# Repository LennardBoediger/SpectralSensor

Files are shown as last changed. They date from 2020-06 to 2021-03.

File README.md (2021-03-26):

# Spectral Measurement Platform
## This is my Bachelorthesis: "Entwicklung und Realisierung eines Messsystems mit den Sensoren AS7261 und AS72651 von AMS"

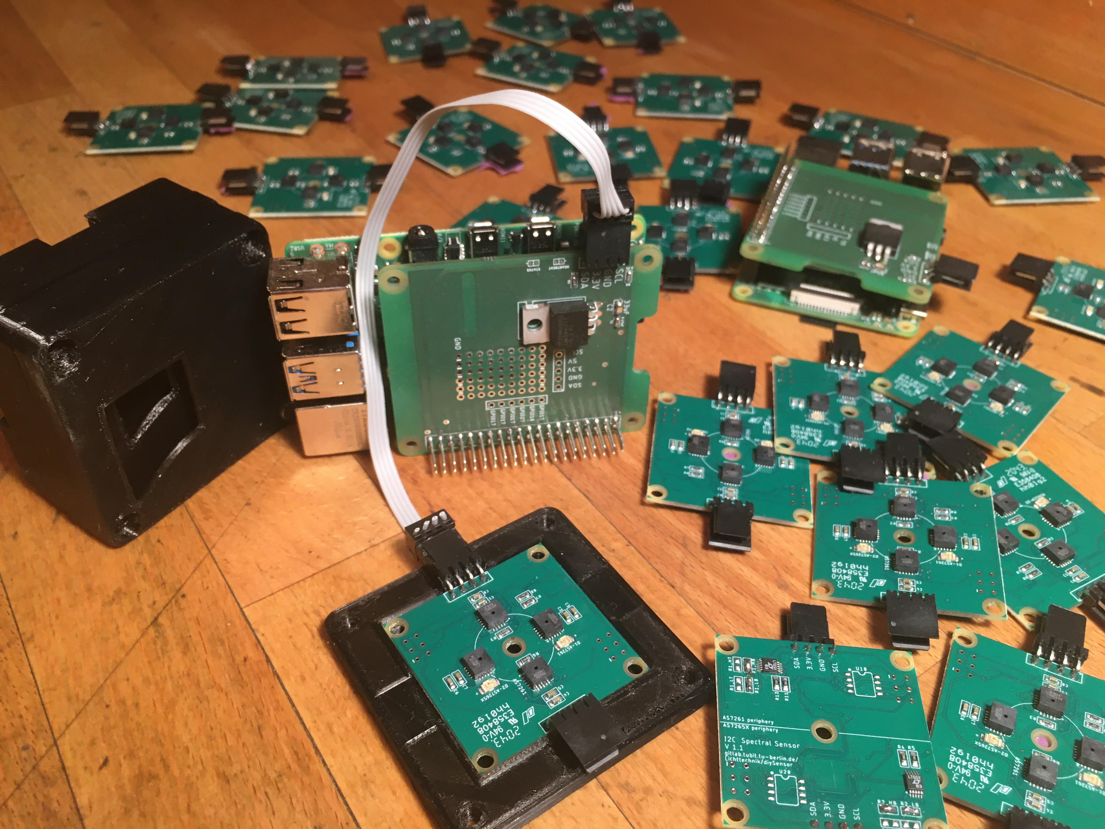
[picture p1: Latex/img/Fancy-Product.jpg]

The goal of this work is to develop a spectral sensor platform using the AS7261 and AS72651, which can be used modularly for different 
research purposes, but especially for sky measurements. Since it is not possible to measure in several directions in the sky at the same 
time with only one of the AS7261 (or AS72651) sensors without mechanical components, it must be ensured that a large number of sensors can be 
combined into a sensor array in order to be able to measure with directional resolution. The resulting sensor platform uses a Raspberry Pi 4 as central 
control unit, which communicates with external sensor boards via I2C.

The final sensor platform will be able to differentiate 21 spectral channels of incident light from up to 20 different directions.

## Grafana WebInterface 

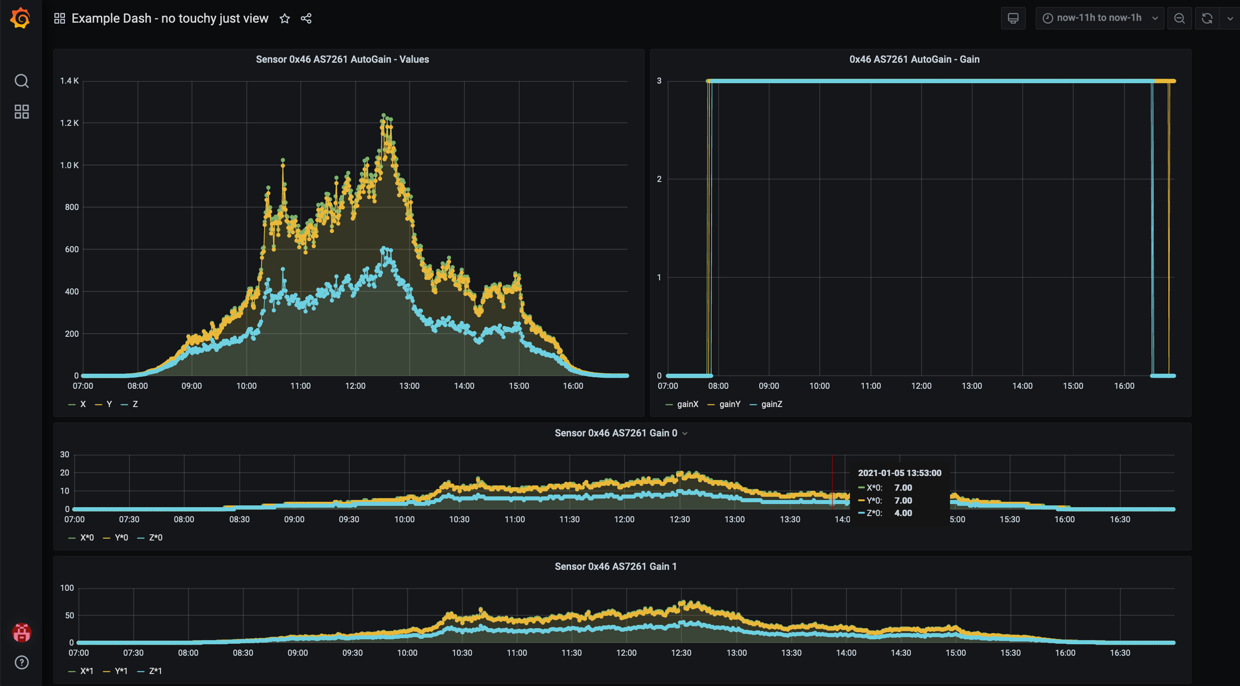
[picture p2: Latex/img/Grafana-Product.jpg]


## Auto Gain
To increase the usable light intensity range, the AutoGain mode can be used.</br>
Measurements are made in all 4 possible gains, the most accurate measured value is selected for each channel. This value is adjusted to the maximum gain with the function matchValueTo-MaxGain to allow a continuous representation of the output.
```c
for (uint8_t gain_i = 0; gain_i < 4; ++gain_i){         // going through every gain
                settings(s[i].address, integrationValue, gain_i); // apply settings integrationValue is fix gain is 0-3
                MeasurementFromAdress(s[i].address);            // initiate measurement from current adress
                AS7261_measurement[gain_i] = getAS7261Measurement(s[i].address, measurement_time, gain_i, 1);    // get data and save to array
            }
            
```

## Usage
Flash the SD image</br>
Attach 1-20 Sensorboards in sereries</br>
Connect to the Pi over SSH</br>
start a detachable screen </br>
make compiles and runs the software</br>
</br>
ssh pi@[IP-ADRESSE]</br>
git clone https://github.com/LennardBoediger/SpectralSensor</br>
cd SpectralSensor </br>
screen</br>
make</br>

Attatch the screen with `screen -r`</br>
Follow the instructions to change the setting and start the measurement</br>
The Webinterface can be found at port 3000 `http://[RASPBERRY_PI-IP]:3000`
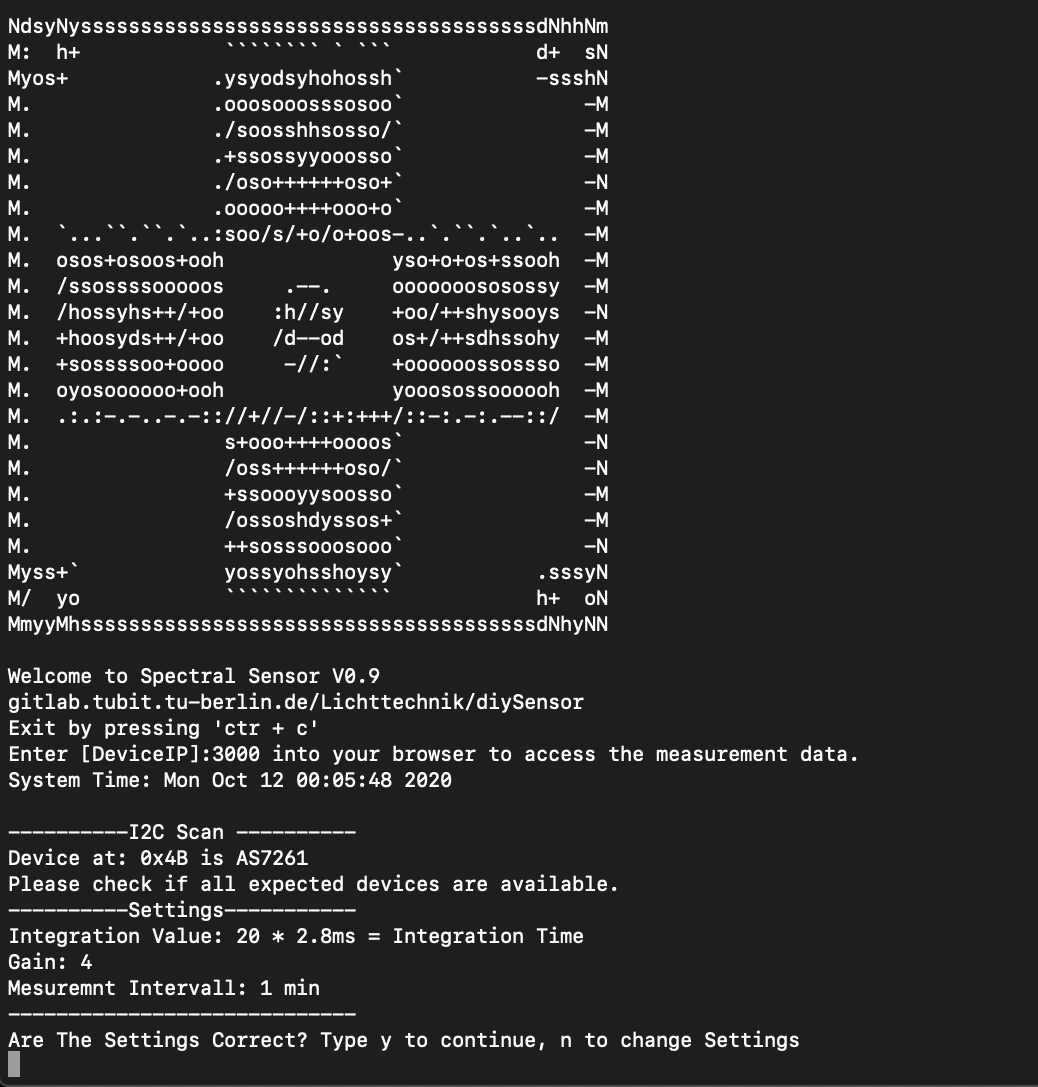
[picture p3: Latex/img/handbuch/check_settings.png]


# Hardware
### Sensorboard
I2C Lanes in Red.</br>
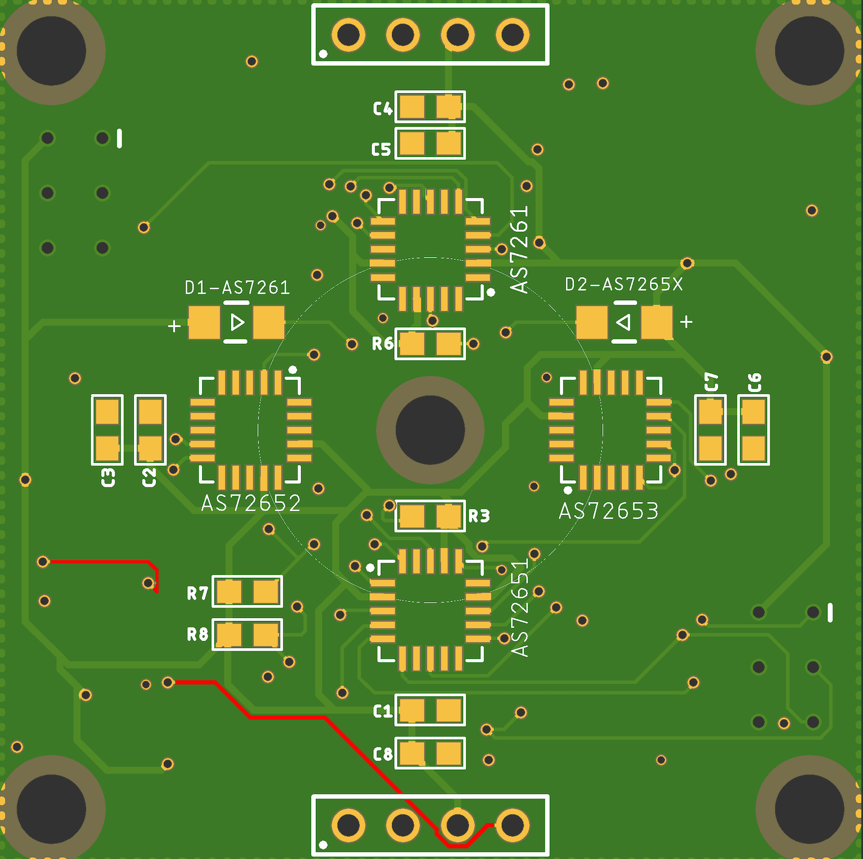
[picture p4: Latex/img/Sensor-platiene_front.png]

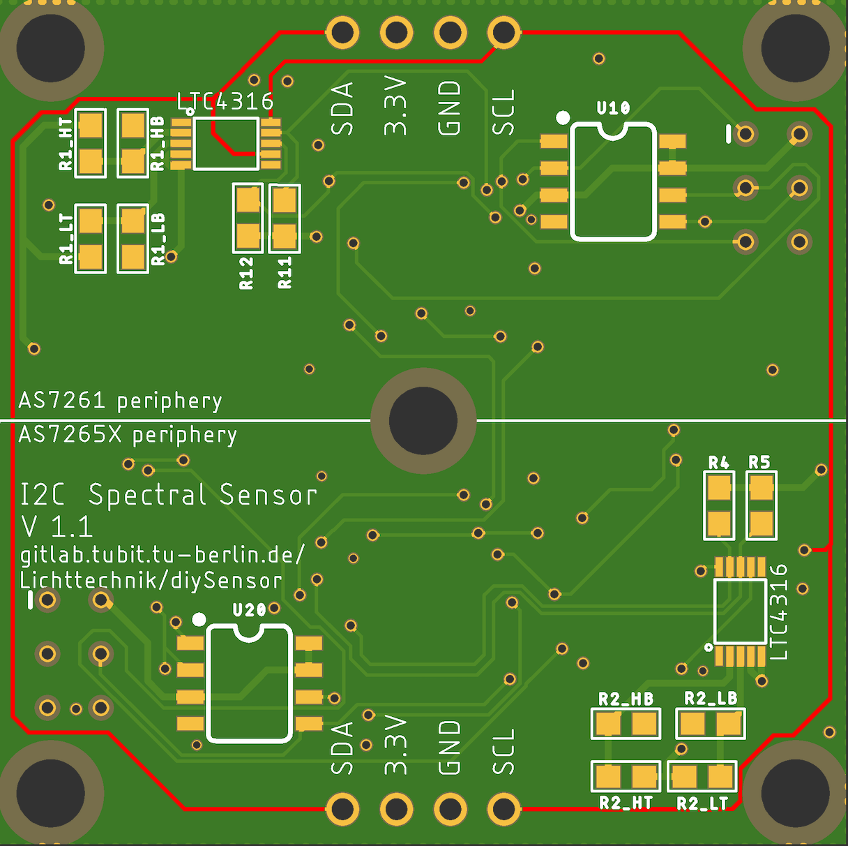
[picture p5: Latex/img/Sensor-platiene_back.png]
right

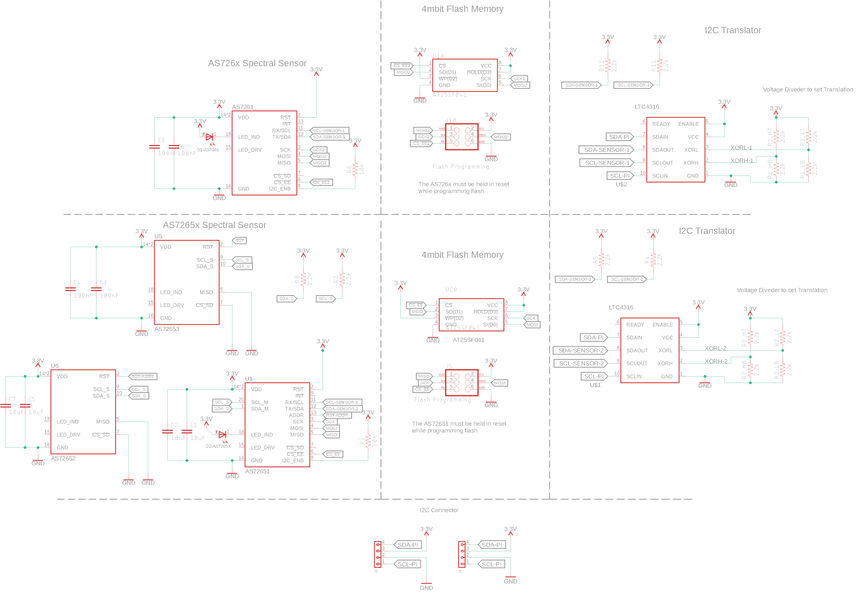
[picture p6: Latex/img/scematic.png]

### Pi-Shield
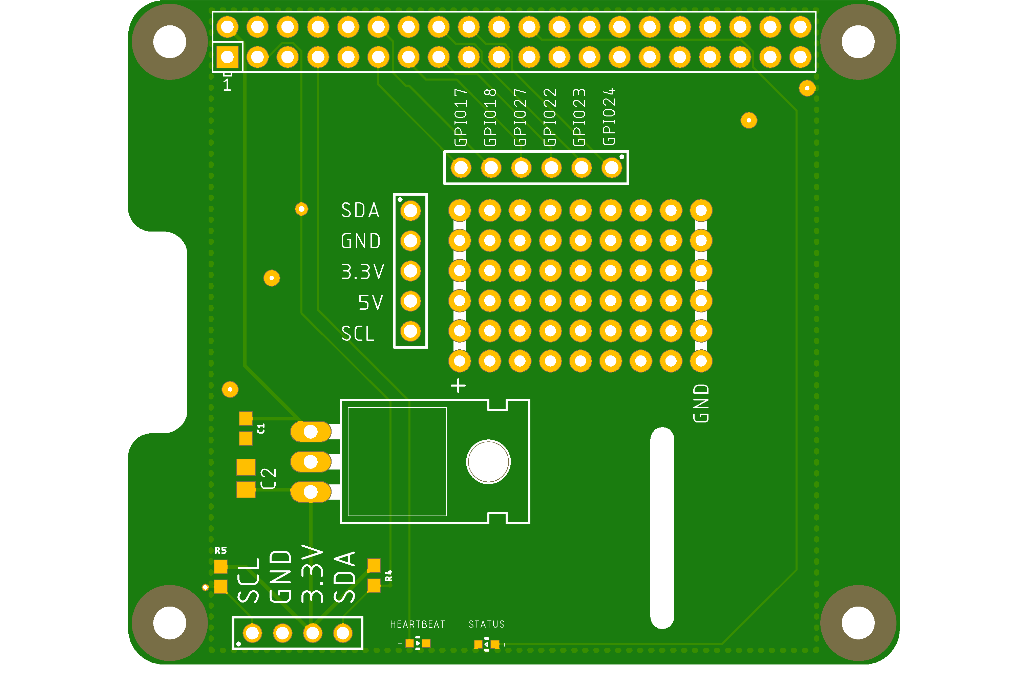
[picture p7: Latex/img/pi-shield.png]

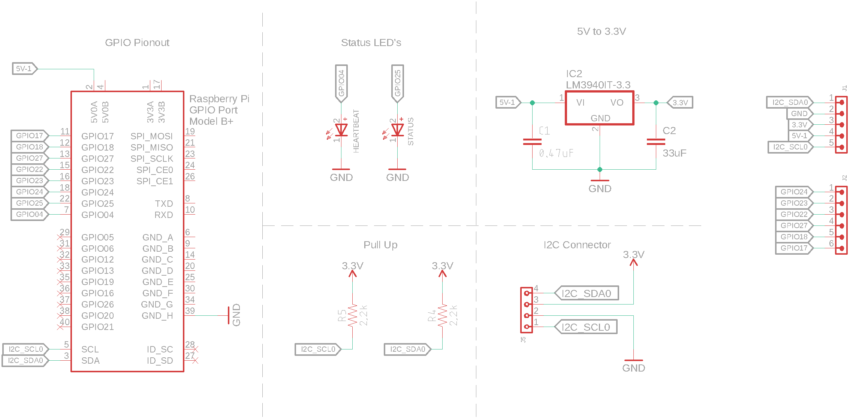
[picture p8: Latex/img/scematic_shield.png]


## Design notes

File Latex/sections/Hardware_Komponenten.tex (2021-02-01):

\subsection{Sensoren}\label{Sensoren}

\begin{wrapfigure}{R}{0.3\textwidth}
\centering
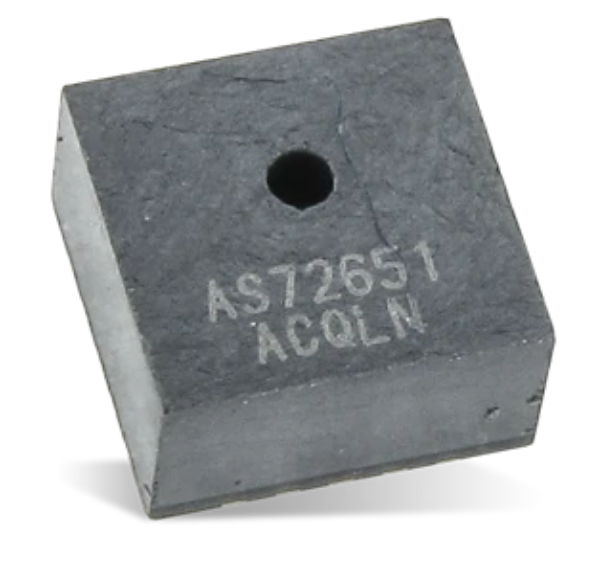
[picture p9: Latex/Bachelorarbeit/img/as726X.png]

 \caption{AS726X \cite{Datenblatt_AS7265X}}
\label{fig:AS726X}
\end{wrapfigure}

Die Sensoren aus der AS726X Reihe sind in der Lage Licht, also elektromagnetische Strahlung, zu messen. 
In jedem Sensor sind 6 Photodioden verbaut. 
Vor jeder Photodiode ist ein Silizium-Interferenzfilter montiert, welcher wie ein Bandpassfilter arbeitet. Er ist nur für einen bestimmten Ausschnitt des Lichtspektrums durchlässig.
Jeder Baustein enthält einen Analog-Digital-Wandler mit 16 Bit Auflösung, der den Photostrom aus den Fotodioden integriert. Nach Abschluss einer Messung wird das integrierte Ergebnis in die entsprechenden RAW Data Register übertragen.\\
So kann über das beschriebene Sensorarray die farbliche Zusammensetzung des eingestrahlten Lichts erfasst werden.

\begin{figure}[H]
\centering
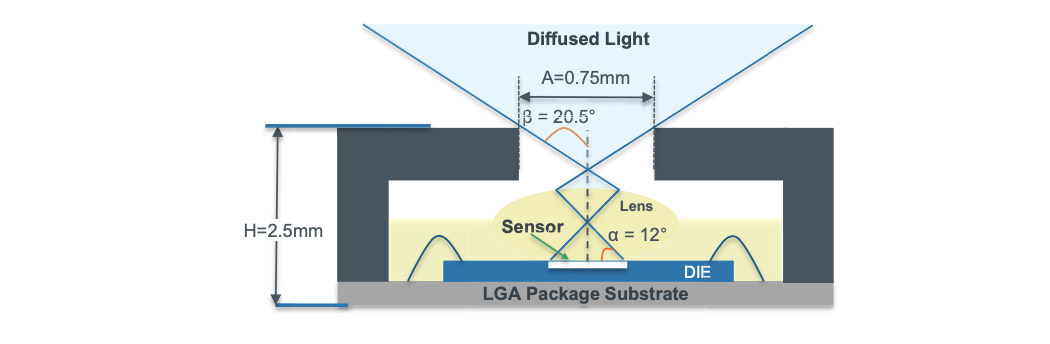
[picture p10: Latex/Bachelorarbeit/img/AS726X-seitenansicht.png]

\caption{Seitenasicht AS726X\cite{Datenblatt_AS7265X}}
\label{fig:Seitenasicht-AS726X}
\end{figure}

\noindent Wie in Abbildung \ref{fig:Seitenasicht-AS726X} dargestellt, fällt das Licht durch die Öffnung in der Mitte des Sensors ein. Eine intern verbaute Linse verteilt das Lich auf die Interferenzfilter. Die Genauigkeit der Filter verändert sich je nach Einstrahlwinkel, daher ist es wichtig vor den Sensor noch eine Streuscheibe zu montieren.\\
Die so gemessenen Daten können über UART oder I2C an einen Mikrocontroller übertragen werden. Da über UART nur ein Gerät verbunden werden kann, eignet sich aber für diesen Anwendungsfall nur die I2C Schnittstelle.\\
\newpage
\noindent Alle Sensoren erhalten vom Hersteller dieselbe, nicht veränderbare I2C Adresse: 0x49. Daher muss ein I2C Translator genutzt werden, welcher es ermöglicht mehrere Sensoren im gleichen Bussystem zu adressieren (siehe Abschnitt \ref{I2C-Translator}).\\

\noindent Die Modelle unterscheiden sich durch die verbauten Silizium-Interferenzfilter, also die unterscheidbaren Wellenlängenbereiche sowie in der benötigten Peripherie.
Die grundsätzliche Messmethode ist aber immer gleich.
Im Folgenden werden die verwendeten Sensoren AS7261 (siehe Abschnitt \ref{AS7261}) sowie der AS7265X (siehe Abschnitt \ref{AS7265X}) beschrieben.\\
Intern im Sensor werden aus den RAW-Werten kalibrierte Werte berechnet, jedoch wird keine ausreichende Dokumentation bereitgestellt.
Daher konnte keine konsistente Korrelation zwischen RAW- und kalibrierten Werten ermittelt werden, weshalb sie im Messaufbau nicht verwendet werden.

%\begin{wrapfigure}{L}{0.3\textwidth}
%\centering
%    \caption{Seitenasicht AS726X}
% \includegraphics[width=0.7\textwidth]{img/AS726X-seitenansicht.png}
% \caption*{Quelle: Datenblatt AS7261}
%  \label{fig:AS726X}
%\end{wrapfigure}
\newpage
\subsubsection{AS7261}\label{AS7261}
Das Sensorarray des AS7261 unterscheidet zwischen X, Y, Z, Clear, Dark und NIR.
Wobei X, Y und Z nach CIE 1931 definiert sind.
Clear ist eine Fotodiode ohne Filter.
Dark ist eine abgedunkelte Fotodiode und wird nur verwendet um störende Einflüsse zu detektieren.
NIR steht für Near-infrared  (Nah-Infrarot).\\

\begin{figure}[H]
  \centering
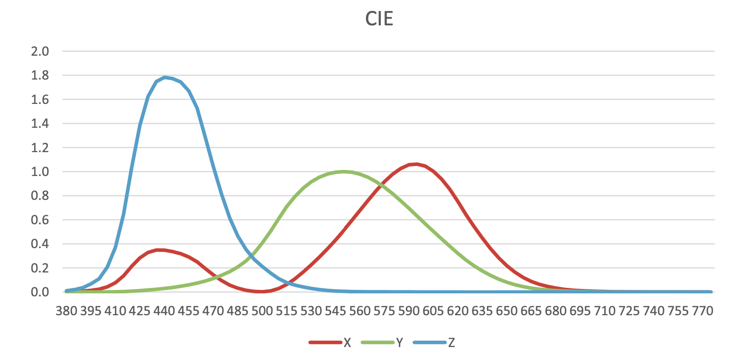
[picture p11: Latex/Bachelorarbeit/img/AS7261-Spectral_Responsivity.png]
 
  \caption{AS7261 Spektrale Empfindlichkeit von X,Y,Z \cite{Datenblatt_AS7261}}
  \label{fig:AS7261-Spectral_Responsivity}
\end{figure}

\begin{wrapfigure}{R}{0.6\textwidth}
\centering
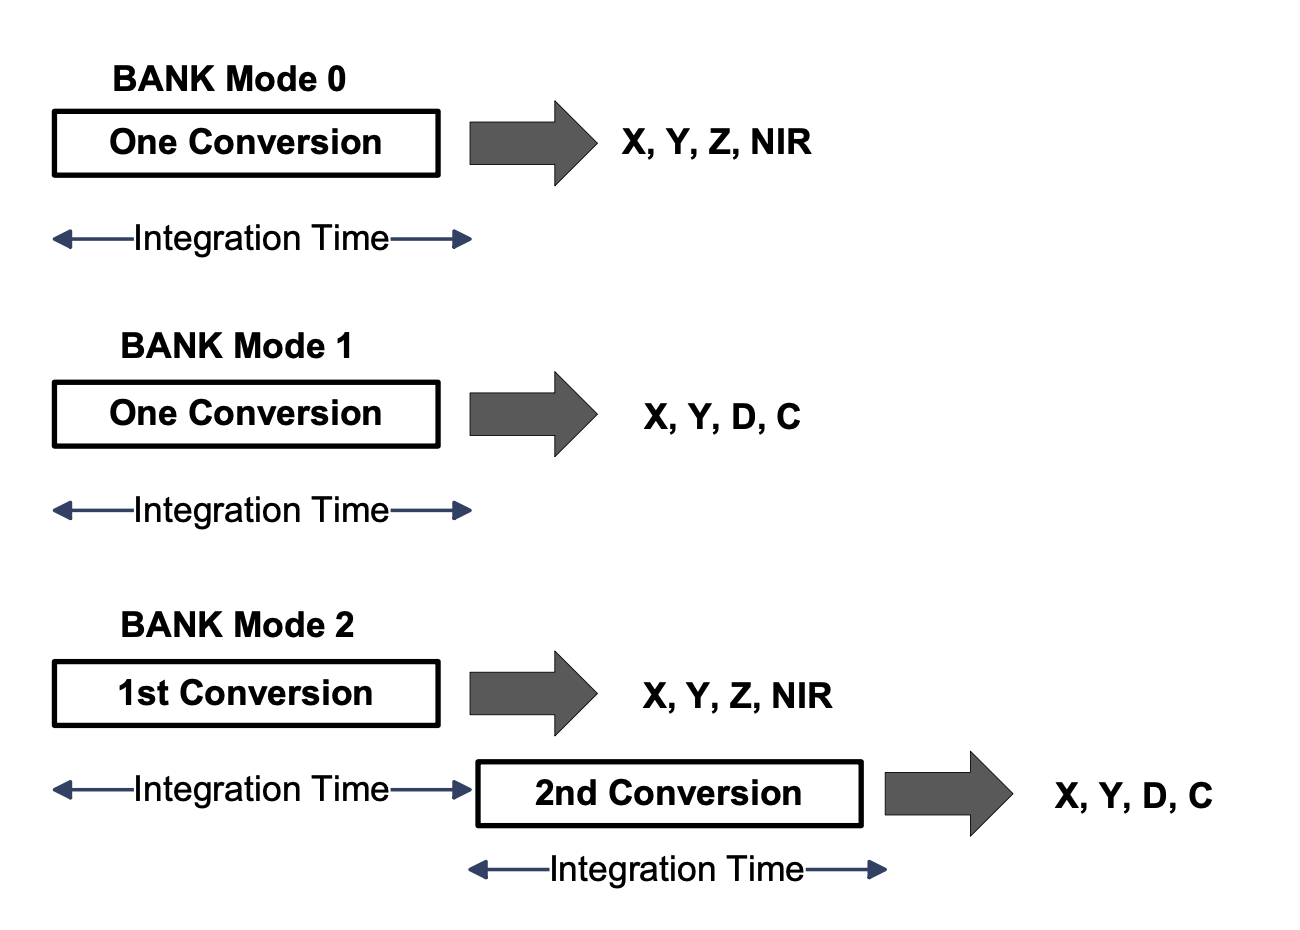
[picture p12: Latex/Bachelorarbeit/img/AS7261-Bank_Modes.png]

\label{fig:AS7261-Bank_Modes}
\caption{AS7261-Bank Modes \cite{Datenblatt_AS7261}}
\end{wrapfigure}

\noindent \textbf{Bank Modes:}\\
\label{sec_bank_modes}
Es gibt 3 sogenannte Bank Modes, in denen der Sensor arbeiten kann.\\
\textbf{Bank Mode 0}\\
Die Konvertierungen erfolgen kontinuierlich und Daten sind in den I2C-Registern X, Y, Z und NIR verfügbar.\\
\textbf{Bank Mode 1}\\
Die Konvertierungen erfolgen kontinuierlich und Daten sind in den I2C-Registern X, Y, D und C verfügbar.\\
\textbf{Bank Mode 2}\\
Die Konvertierungen erfolgen kontinuierlich, Daten sind nach zwei Integrationsperioden in den Registern X, Y, Z, NIR, D und C verfügbar. 
In diesem Modus können die kalibrierten, korrigierten Werte auch aus den entsprechenden I2C-Registern abgerufen werden.\\
\newpage
\noindent \textbf{Bank Mode 3}\\
Die Konvertierungen erfolgen nur ein Mal und Daten sind, wie in Bank Mode 2, nach zwei Integrationsperioden in den Registern X, Y, Z, NIR, D und C verfügbar.
Auch die kalibrierten, korrigierten Werte können aus den entsprechenden I2C-Registern abgerufen werden.
Das DATA RDY-Bit wird auf 1 gesetzt, sobald Daten verfügbar sind.\\
Für den hier beschriebenen Messaufbau wird Bankmode 3 verwendet, da so an alle angeschlossenen Sensoren möglichst gleichzeitig eine Messung gestartet werden kann.
Die Daten können nach abgeschlossener Messung an den Raspberry Pi übertragen werden.

\subsubsection{AS7265X}\label{AS7265X}
AS7265X beschreibt AS72651, AS72652 und AS72653 wobei der AS72651 als Master für AS72652 und AS72653 fungiert (Abbildung \ref{fig:S7265X-Scematic}), indem er über einen weiteren separaten I2C Bus ihre Daten abfragt und ansonsten wie der AS7261 arbeitet.
Der angeschlossene Mikrocontroller (Einplatinencomputer) kommuniziert nur mit dem AS72651.

\begin{figure}[H]
  \centering
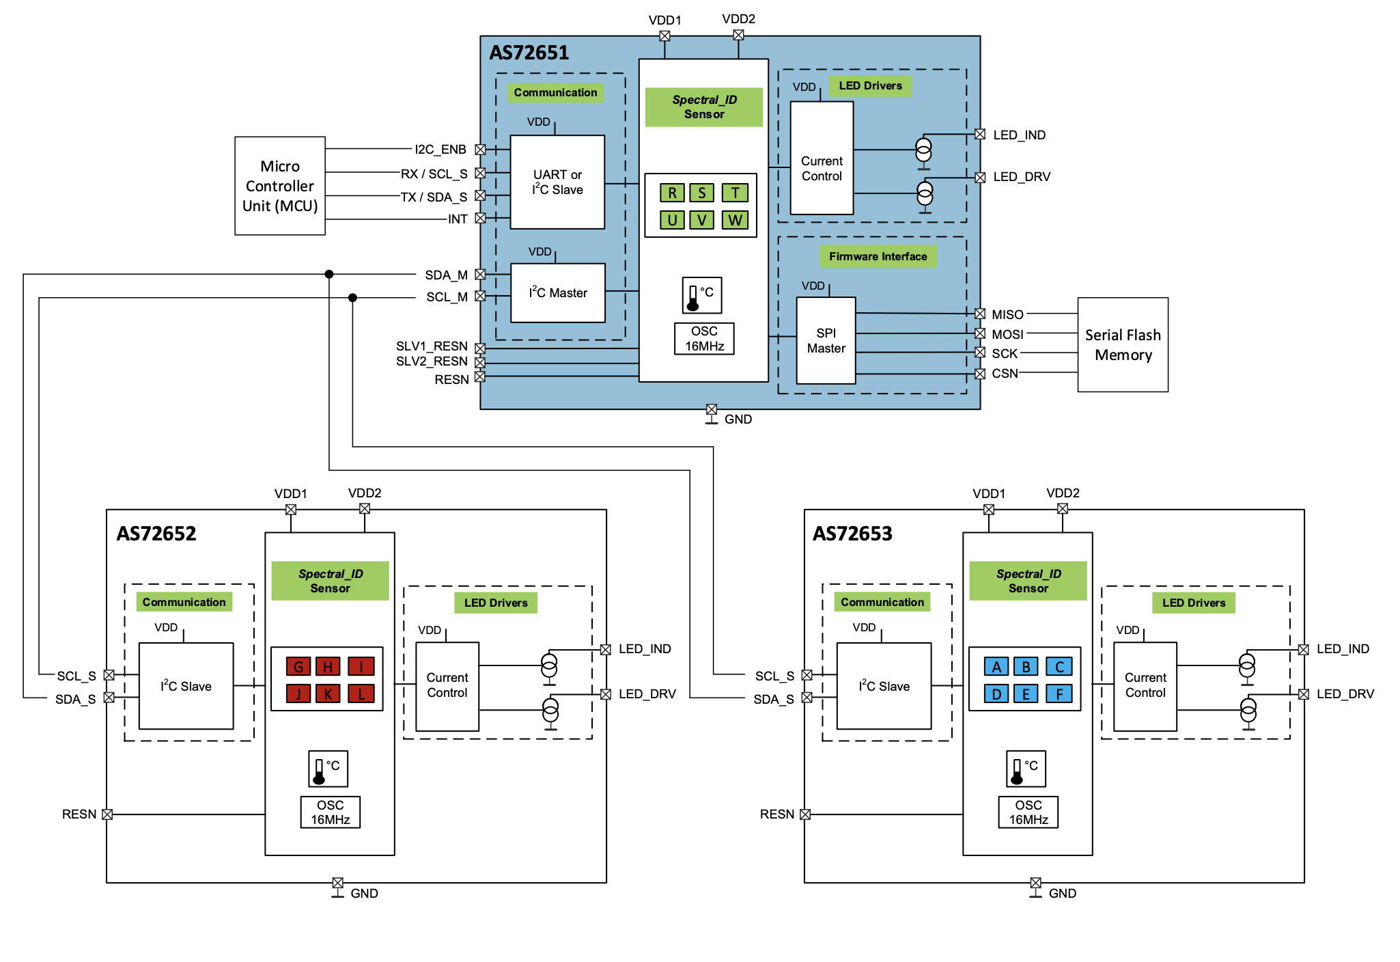
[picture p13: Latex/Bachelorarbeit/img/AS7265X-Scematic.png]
 
 \caption{S7265X-Scematic\cite{Datenblatt_AS7265X}}
  \label{fig:S7265X-Scematic}
\end{figure}

\begin{figure}[H]
  \centering
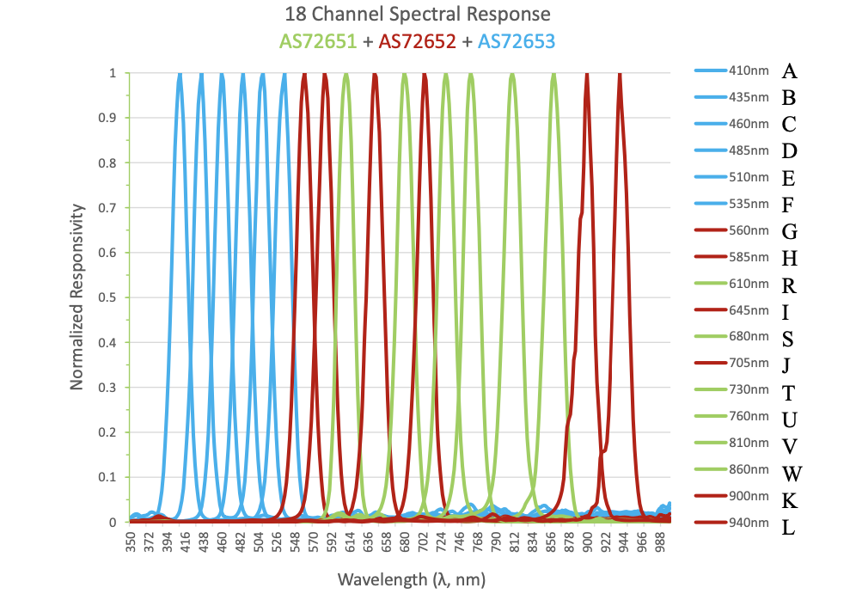
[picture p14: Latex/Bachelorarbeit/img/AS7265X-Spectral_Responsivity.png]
 
 \caption{AS7265X-Spektrale Empfindlichkeit\cite{Datenblatt_AS7265X}}
  \label{fig:AS7261-Spectral_Responsivity}
\end{figure}

\noindent Die drei Sensoren messen in Kombination mit 18  Photodioden mit unterschiedlichen Filtern. So können sie 18 unterschiedliche Frequenz-Channel im Bereich zwischen 410 nm und 940 nm mit einer Halbwertsbreite von jeweils 20 nm erfassen.
Die Frequenz-Channel sind, wie in Abbildung \ref{fig:AS7261-Spectral_Responsivity} zu sehen, mit den Buchstaben A-L gekennzeichnet.\\
Wie der AS7261 kann der AS7265X in 3 Bankmodi betrieben werden, wobei auch für diesen Sensor der Bankmodus 3 verwendet wird, da alle Farbkanäle in einer manuell ausgelösten Messung aufgezeichnet werden sollen.
\newpage
\subsection{Mikrocontroller}\label{Mikrocontroller}
Bei der Auswahl des Mikrocontrollers ist die kleine Bauform, ausreichend langlebiger Speicher sowie eine Netzwerkschnittstelle und I2C Anschluss entscheidend.\\
Die Abfrage der Messdaten sowie die Messkonfiguration soll über einen Fernzugriff möglich sein. Die Daten sollen grafisch in einem Webinterface dargestellt werden, ohne dass eine weitere Serverinstanz benötigt wird. Daher eignet sich ein Linux-Fähiger Einplatinencomputer besser als ein simplerer Mikrocontroller.
Außerdem ermöglicht ein Einplatinencomputer einfache nachträgliche Änderungen, ohne dass eine komplexe Entwicklungsumgebung eingerichtet werden muss.\\

Der Raspberry Pi 4 Model B erfüllt alle diese Anforderungen:

\begin{center}
\begin{tabular}{ c c }
 Abmessungen & 85.6 mm × 56.5 mm \\ 
 Speicher & eMMC Flash Module Socket \\  
 Anschlüsse & Gigabit Ethernet, USB, WLAN \\  
 GPIO & UART, I2C, IO \\  
 RAM & 2 GB \\  
 CPU & Broadcom BCM2711 ARM Cortex A72 \\  
 Preis & 37€ (+20€ für Netzteil und 32GB SD-Karte)  
\end{tabular}
\end{center}
\begin{figure}[H]
  \centering
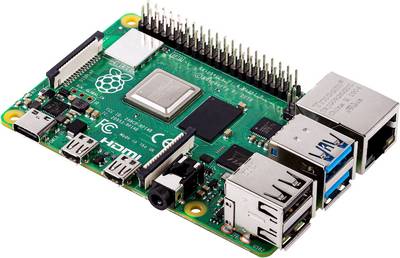
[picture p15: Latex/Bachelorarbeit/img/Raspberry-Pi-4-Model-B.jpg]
 
	\caption{Raspberry Pi 4 Model B \cite{raspberrypi_fundation}}
  \label{fig:Raspberry_Pi_4_Model_B}
\end{figure}
An den SD-Kartenslot kann bis zu 256 GB Flash-Speicher angeschlossen werden.
Ein Sensorboard erzeugt etwa 0,73 MB Daten pro Tag.
Bei 12 Sensorboards ist eine noch höhere Effizienz der Datenkomprimierung zu erwarten. Wenn trotzdem 8,78 MB pro Tag angenommen werden, benötigt der Messaufbau maximal 3,3 GB pro Jahr.
Das Betriebssystem, inklusive aller verwendeten Systemkomponenten, benötigt 3,9 GB.
Im Messaufbau werden 32GB SD-Karten verwendet.\\
Die Internetverbindung kann über WLAN oder Ethernet hergestellt werden.
Da eine kabelgebundene Lösung mehr Zuverlässigkeit bietet, wird eine Netzwerkverbindung über Ethernet einer WLAN-Schnittstelle vorgezogen.\\
Die GPIO des Raspebrry Pi arbeiten mit 3,3V.
Der 3,3V Pin des Raspebrry Pi stellt nur 850mA am 3,3V Output bereit.
Da jedes Sensorboard etwa 170 mA benötigt, reichen 850 mA nicht für die maximale Anforderung von 10 Boards aus.
Der 5V-Pin ist direkt mit dem Netzteil verbunden und kann daher genauso viel Leistung wie das Netzteil liefern. Mithilfe eines Abwärtswandlers ist es möglich, die Sensorplatinen mit 3,3V zu betreiben.\\
Die CPU ist für den Anwendungsfall weitaus ausreichend dimensioniert.
In Abbildung \ref{fig:CPU-Performance} ist ein Performancetest zu sehen Die Reihen 1-4 beschreiben die prozentuale CPU Auslastung der jeweiligen Prozessorkerne.
MEM beschreibt die Auslastung des Arbeitsspeichers.\\
Für den Performancetest wurde eine Messung an 4 Sensor Boards mit minimalem Messintervall gestartet.
Außerdem wurden gleichzeitig Daten über Grafana exportiert.\\
\begin{figure}[H]
  \centering
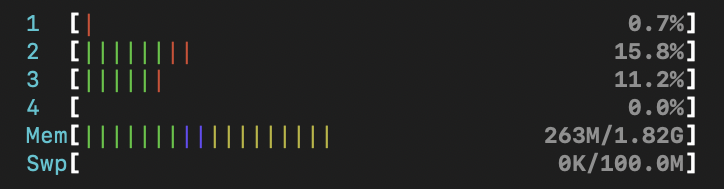
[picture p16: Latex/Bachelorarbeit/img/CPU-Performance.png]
  
  \caption{Screenshot: CPU-Performance}
  \label{fig:CPU-Performance}
\end{figure}
\noindent Der prozentuale Lastdurchschnitt über die letzten 5 Minuten während des Tests wird mit 0,89\% angegeben.

\subsection{I2C Address Translator LTC4316}\label{I2C-Translator}
Da wie in Abschnitt \ref{Sensoren} genannt, alle Sensoren unter derselben I2C Addresse erreichbar sind, wird ein I2C Translator genutzt, um für eine individuelle Adressierung zu sorgen.\\

\begin{figure}[H]
  \centering
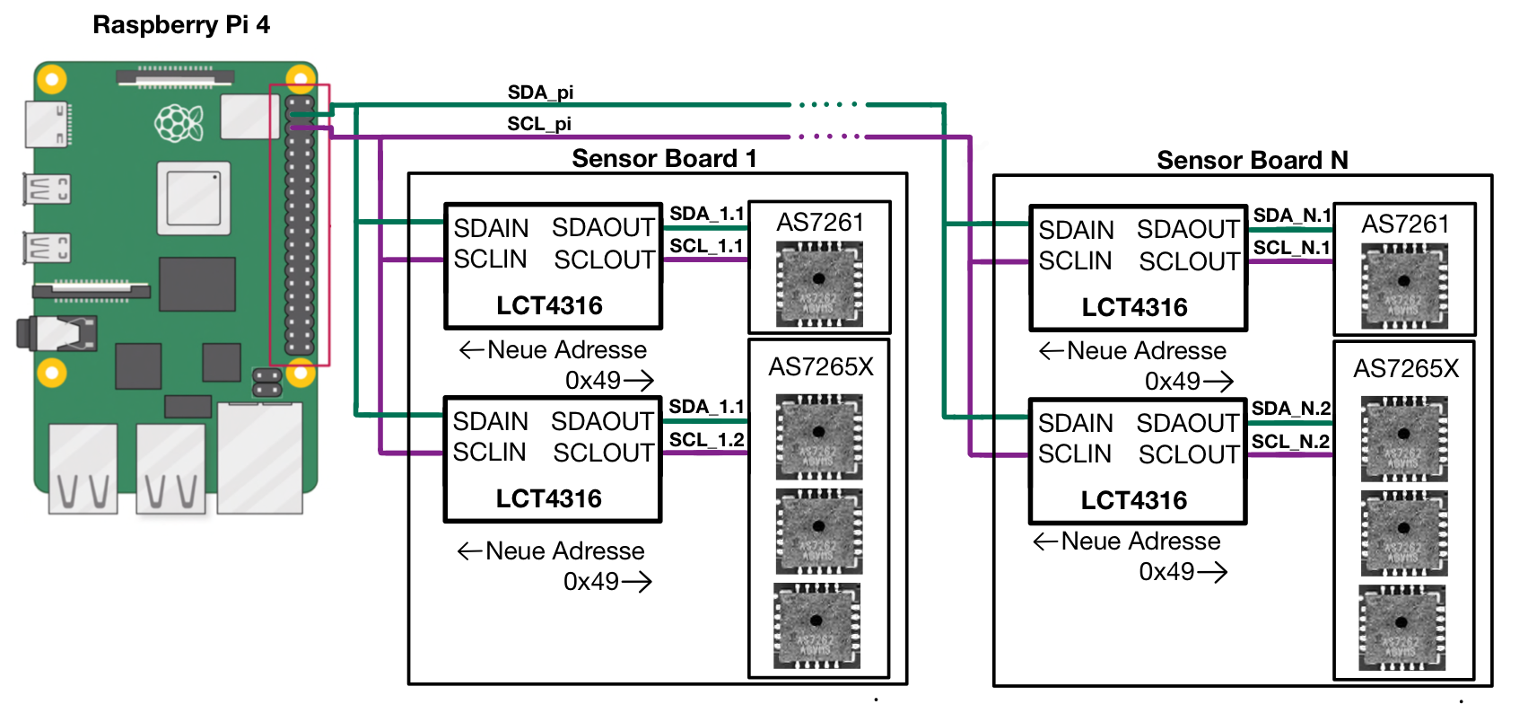
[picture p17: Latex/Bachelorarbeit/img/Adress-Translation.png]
 
  \caption{I2C-Bus im Messaufbau \cite{raspberrypi_fundation}}
    \label{fig:adress-translation}
\end{figure}

\noindent Wie in Abbildung \ref{fig:adress-translation} zu sehen, wird für jeden Sensor ein LTC4316 an die Busschnittstelle des Raspberry Pi angeschlossen (SDAIN, SCLIN).\\ 
An jeden LTC4316 wird ein AS7261 oder AS72651 angeschlossen (SDAOUT, SCLOUT).
Bei Kommunikation vom Raspberry Pi zum Sensor wird dann die I2C Adresse mit einem Faktor (Translation Byte), welcher mit diskreten Widerständen eingestellt wird, mit Fomel (\ref{I2C-translation}) verrechnet, um so die Adresse anzupassen (XORH,XORL).
Um das Translation Byte einzustellen, müssen die Widerstände $R_{HT}$, $R_{LT}$, $R_{HB}$ und $R_{LB}$ wie in Abbildung \ref{fig:Translation-Byte} am LTC4316 angeschlossen werden.

\begin{equation} 
\label{I2C-translation}
Sensor Adresse\oplus TranslationByte = NeueAdresse \footnote{xor = $\oplus$}
\end{equation}

\begin{wrapfigure}{R}{0.6\textwidth}
\centering
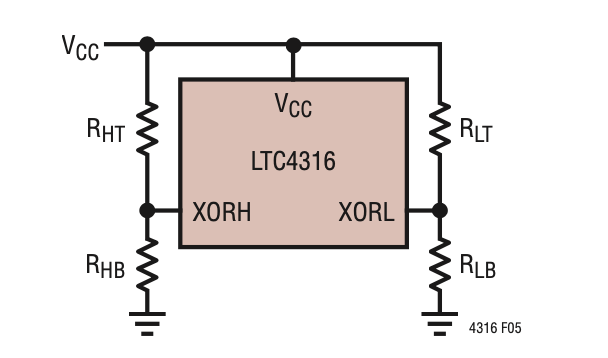
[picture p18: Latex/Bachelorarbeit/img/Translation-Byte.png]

\caption{Translation Byte\cite{Datenblatt_LTC4316}}
\label{fig:Translation-Byte}
\end{wrapfigure}
\bigskip

Beispiel Rechnung\\
$0x49 \oplus 0x01 = 0x48$\\
$0x49 \oplus 0x02 = 0x4b$\\
$0x49 \oplus 0x05 = 0x4c$\\
$0x49 \oplus 0x06 = 0x4f$\\
$0x49 \oplus 0x0A = 0x43$\\
$0x49 \oplus 0x49 = 0x00$\\

\newpage

\noindent 
Tabelle \ref{TranslationByte_Lower} enthält die erforderlichen Widerstandswerte für die diskreten Widerstände $R_{LT}$ und $R_{LB}$ und die daraus resultierenden unteren 4 Bits des Translationsbytes.
Tabelle \ref{TranslationByte_Upper} enthält die erforderlichen Widerstandswerte für die diskreten Widerstände $R_{HT}$ und $R_{HB}$ und die daraus resultierenden oberen 4 Bits des Translationsbytes.

\noindent Durch das Anlöten der jeweiligen Wiederstande können alle 128 mögliche Kombinationen für das Translation Byte erreicht werden. (128 Möglichkeiten ergeben sich da Bit a7 immer 0 ist.) 

\noindent Im Handbuch (Abschnitt \ref{liste_Translationbytes}) ist aufgelistet welche, Translation Bytes bereits verwendet werden. Wenn weitere Sensor-Boards angefertigt werden, ist die Liste dort weiter zu pflegen.

\begin{table}[!ht]
\caption{Untere 4 Bit des Translation Byte}
\label{TranslationByte_Lower}
\centering
\begin{tabular}{c|c|c|c|c|c}
 a3 & a2 & a1 & a0 & $R_{LT}$[$k\Omega$] & $R_{LB}$[$k\Omega$]\\
 0 & 0 & 0 & 0 & Open & Short \\ 
 0 & 0 & 0 & 1 & 976 & 102\\ 
 0 & 0 & 1 & 0 & 976 & 182\\
 0 & 0 & 1 & 1 & 1000 & 280\\ 
 0 & 1 & 0 & 0 & 1000 & 392\\ 
 0 & 1 & 0 & 1 & 1000 & 523\\ 
 0 & 1 & 1 & 0 & 1000 & 681\\ 
 0 & 1 & 1 & 1 & 1000 & 887\\
 1 & 0 & 0 & 0 & 887 & 1000 \\ 
 1 & 0 & 0 & 1 & 681 & 1000\\ 
 1 & 0 & 1 & 0 & 523 & 1000\\
 1 & 0 & 1 & 1 & 392 & 1000\\ 
 1 & 1 & 0 & 0 & 280 & 1000\\ 
 1 & 1 & 0 & 1 & 182 & 976 \\ 
 1 & 1 & 1 & 0 & 102 & 976\\ 
 1 & 1 & 1 & 1 & Short & Open\\
\end{tabular}
\end{table}

\begin{table}[H]
\caption{Obere 4 Bit des Translation Byte}
\label{TranslationByte_Upper}
\centering
\begin{tabular}{c|c|c|c|c|c|c}
 a7 & a6 & a5 & a4 & $R_{HT}$[$k\Omega$] & $R_{HB}$[$k\Omega$]\\
 0 & 0 & 0 & 0 & Open & Short \\ 
 0 & 0 & 0 & 1 & 976 & 102\\ 
 0 & 0 & 1 & 0 & 976 & 182\\
 0 & 0 & 1 & 1 & 1000 & 280\\ 
 0 & 1 & 0 & 0 & 1000 & 392\\ 
 0 & 1 & 0 & 1 & 1000 & 523\\ 
 0 & 1 & 1 & 0 & 1000 & 681\\ 
 0 & 1 & 1 & 1 & 1000 & 887\\

\end{tabular}
\end{table}

\subsection{Companion Flash}
\label{sec_Companion_Flash}
Die Sensoren AS7261 und AS72651 benötigen einen Flash-Speicher, von welchem sie ihre Firmware laden können.
Die jeweilige Firmware von AMS wird mithilfe von Flashcat-USB, einem USB Memory Programmer über das SPI (Serial Peripheral Interface), auf den Flash Speicher übertragen.
Ein Leitfaden für diesen Vorgang wird von AMS unter dem Titel ``How to Program AS72xx Firmware with FlashCatUSB'' bereitgestellt und ist im Anhang zu finden.\\
%https://ams.com/documents/20143/36005/AS72xx_AN000488_3-00.pdf/ab1c985f-785f-7431-99d5-ddea807585db
Der AT25SF041-SSHD-B wurde aus der von AMS bereitgestellten Liste kompatibler Flash-Speichern\footnote{AS726x Design Considerations - 2.5 Flash Memory} ausgewählt, da er am günstigsten ist. 
Für den Messaufbau werden folgende Versionen verwendet.

\begin{tabular}{ l|l } 

  Chip  & Firmware \\ 
 \hline
 AS7261  & AS7261\_complete.bin \\ 
 
 AS726X & AS7265\_complete\_moonlight\_v1.bin\\ 

\end{tabular}
\medskip

Die Binary-Files  sind im Anhang zu finden.\\

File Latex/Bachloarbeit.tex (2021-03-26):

\documentclass[a4paper,oneside,12pt,titlepage]{scrartcl}   %Grundeinstellungen

\usepackage[ngerman]{babel}
%\usepackage[T1]{fontenc} % umlaute
\usepackage[utf8]{inputenc}
\usepackage{setspace}
\usepackage{amsfonts}
\usepackage{amsmath}
\usepackage{amssymb}
\usepackage{amsthm}
\usepackage{subfiles} 
\usepackage{caption}
\usepackage{hyperref}
\usepackage{ragged2e}
\usepackage{wrapfig}
\usepackage[amssymb]{SIunits}
\usepackage{cite}
\usepackage[usenames,dvipsnames]{xcolor}
\usepackage{listings}
\usepackage{textcomp}

\definecolor{comment}{RGB}{0,128,0} % dark green
\definecolor{string}{RGB}{255,0,0}  % red
\definecolor{keyword}{RGB}{0,0,255} % blue

\lstdefinestyle{c}{
	commentstyle=\color{comment},
	stringstyle=\color{string},
	keywordstyle=\color{keyword},
	basicstyle=\footnotesize\ttfamily,
	numbers=left,
	numberstyle=\tiny,
	numbersep=5pt,
	frame=lines,
	breaklines=true,
	prebreak=\raisebox{0ex}[0ex][0ex]{\ensuremath{\hookleftarrow}},
	showstringspaces=false,
	upquote=true,
	tabsize=2,
}
 \lstset{language=c} 

\renewcommand{\familydefault}{\sfdefault} 
\usepackage{graphicx}
\usepackage{subcaption}                       
\usepackage{float}
\usepackage[section]{placeins}
\renewcommand{\topfraction}{0.85}
\renewcommand{\textfraction}{0.1}
\renewcommand{\floatpagefraction}{0.75}

\usepackage{cite}
\usepackage[usenames,dvipsnames]{xcolor}

\usepackage{listings}

\lstset{%
	 basicstyle=\scriptsize\ttfamily,
   keywordstyle=\bfseries\ttfamily\color{NavyBlue},
   stringstyle=\color{Rhodamine}\ttfamily,
   commentstyle=\color{Green}\ttfamily,
   emph={square}, 
   emphstyle=\color{blue}\texttt,
   emph={[2]root,base},
   emphstyle={[2]\color{yac}\texttt},
   language=Python,%
   tabsize=2,%
   basicstyle=\footnotesize\ttfamily,%
   numbers=left,%
   numberfirstline,%
   breaklines=true,%
   breakatwhitespace=true,%
   linewidth=\textwidth,%
   xleftmargin=0.075\textwidth,%
   frame=tlrb,%
   captionpos=b%
}

%Header Definitionen
\usepackage{fancyhdr}
\renewcommand{\headrulewidth}{0.5pt}
\renewcommand{\footrulewidth}{0.5pt}
%Abstand zwischen Absätzen, Zeilenabstände
\voffset26pt 
\parskip6pt
%\parindent1cm  %Rückt erste Zeile eines neuen Absatzes ein
\usepackage{setspace}
\onehalfspacing

\begin{document}
\pagenumbering{arabic}

% Titeseite
\begin{titlepage}
\begin{center}
	\begin{minipage}{0.6\textwidth}
	\begin{tabular}{l}
	Technische Universität Berlin\\
	Fakulät IV (Elektrotechnik und Informatik)\\
	Institut für Energie- und Automatisierungstechnik\\
	Fachgebiet Lichttechnik\\
	\end{tabular}
	\end{minipage}
	\hfill
	\begin{minipage}{0.3\textwidth}\raggedright
	\\
	\end{minipage}
	
	\vspace{3cm}
    \sffamily \LARGE \textbf{Entwicklung und Realisierung einer Messeinrichtung mit den Sensoren AS7261 und AS72651 von ams}\\
 	\Large Bachelorarbeit\\
    \vspace{2.5cm}
	{\renewcommand{\arraystretch}{0.7}
    	\begin{tabular}{ll}
    		Vorgelegt von: & Lennard Bödiger\\
			Studiengang:	 & Technische Informatik\\
			Matrikel-Nr.: & 363470\\
		\end{tabular}
	}

  	\vspace{5.3cm}
	\end{center}
	\begin{tabular}{ll}
		Eingereicht am: & 8. Februar 2021\\
		Betreuung: & Nils Weber\\
		Prüfer/in: & Prof. Dr.-Ing. Stephan Völker \\ 	&Prof. Dr.-Ing. Sibylle Dieckerhoff
	\end{tabular}\\
\end{titlepage}
\newpage
\begin{figure}[H]
\centering
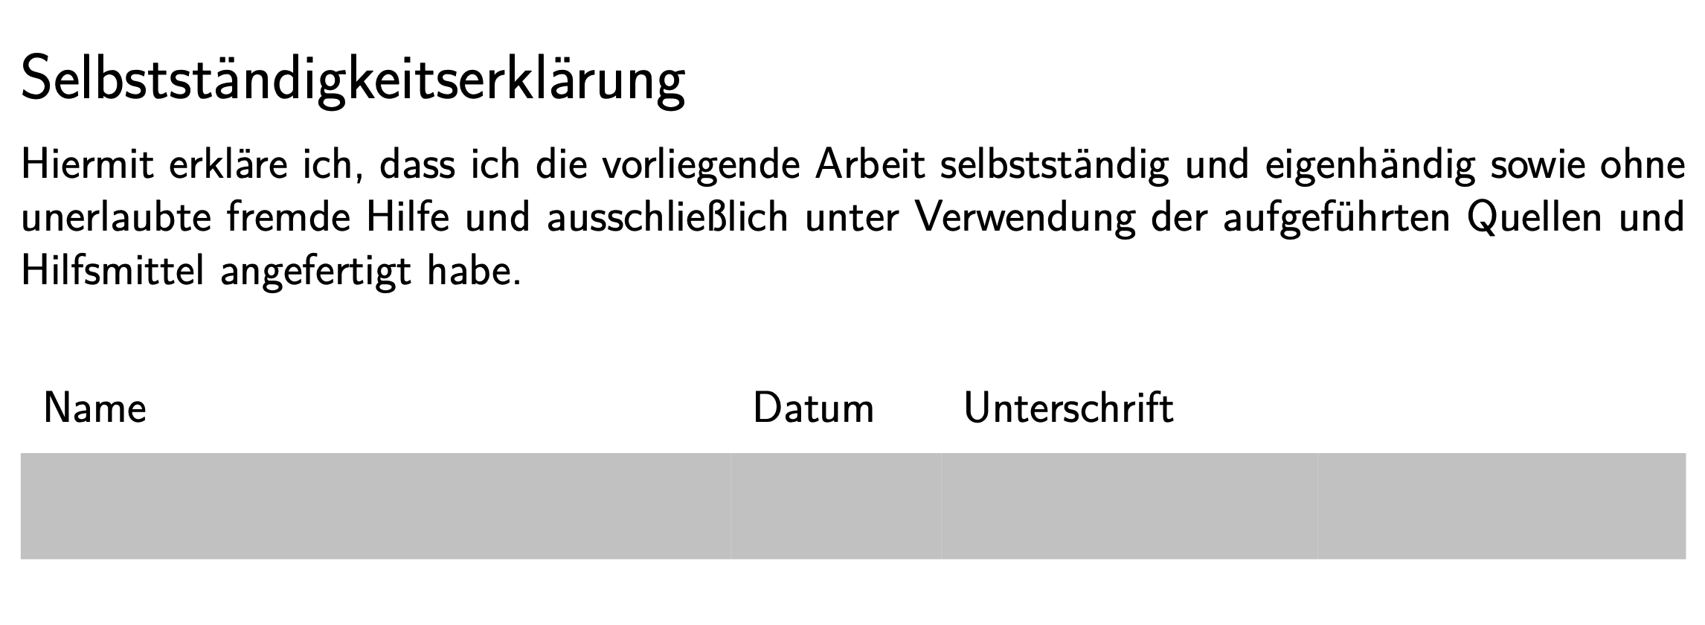
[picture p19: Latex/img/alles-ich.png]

\end{figure}

\newpage

\section*{Abstract}
\subfile{sections/Abstract}
\newpage
\tableofcontents
\newpage
\listoffigures
\newpage
\listoftables
\newpage

\section{Einleitung}
\subfile{sections/Einleitung}
\newpage
\section{Technische Grundlagen}
\subfile{sections/Technische_Grundlagen}
\newpage
\section{Hardware Komponenten}
\subfile{sections/Hardware_Komponenten}
\newpage
\section{Platine}
\subfile{sections/Platine}
\newpage
\section{Datenbank \& Webinterface}
\subfile{sections/Datenbank_und_Webinterface}
\newpage
\section{C Code}
\subfile{sections/Software}
\newpage
\section{Benutzerhandbuch}
\subfile{sections/Benutzerhandbuch}
\newpage
\section{Messungen}
\subfile{sections/Messungen}
\newpage
\section{Zusammenfassung}
Der Raspberry Pi hat sich als Steuergerät für den Messaufbau bewährt.
Der Programmcode kann schnell und einfach über SSH ausgeführt werden und auch die Fehlersuche ist sehr komfortabel.\\
Grafana lässt sich in der grafischen Oberfläche sehr einfach anpassen. Jedoch ist das einmalige Einrichten eines Dashboards für viele Sensoren umständlich und zeitaufwendig.
Die Datenkomprimierungseffizienz von InfluxDB übertrifft die Erwartungen, so dass es möglich ist, auch mit kleinen SD-Karten über mehrere Jahre Daten zu erfassen.\\
Alle Softwarekomponenten laufen im Dauertest mit einer angeschlossenen Sensorplatine seit sechs Wochen ohne Probleme.
In einem weiteren Test läuft das System mit 4 angeschlossenen Sensorboards seit zwei Wochen ebenfalls ohne Probleme.\smallskip

\noindent Zum Abgabezeitpunkt der vorliegenden Arbeit besteht das Problem, dass nur vier Sensorplatinen, d.h. 8 I2C-Slaves, gleichzeitig am Bus angeschlossen werden können.
Ab dem fünften Sensorboard kann der Raspberry Pi die I2C-Adressen der angeschlossenen Sensoren nicht mehr finden.
Als Workaround gibt es die Möglichkeit, einen Bus-Multiplexer zu verwenden.
Dieses Gerät wird über I2C direkt an den Bus angeschlossen und hat mehrere I2C-Bus-Ports. Über einen Befehl kann dem Multiplexer mitgeteilt werden, welcher I2C-Bus-Kanal zum Raspberry Pi durchgeschaltet wird.
Eine Betaversion des Workarounds ist bereits implementiert und auf Github\footnote{\url{https://github.com/LennardBoediger/SpectralSensor}} zu finden, wird aber in dieser Arbeit nicht behandelt.
\smallskip

\noindent Abgesehen davon, dass die geforderte Anzahl der anschließbaren Sensoren derzeit nicht erreicht wird, ist der Messaufbau einsatzbereit und die verbleibenden Probleme können mit überschaubarem Aufwand gelöst werden.
\newpage
\bibliography{Quellen/Quellen.bib}
\bibliographystyle {ieeetr}
\newpage
\section*{Anhangsverzeichnis}

\noindent \textbf{AMS\_Firmware}\\
\indent AS7261\_complete.bin\\
\indent AS7265\_complete\_moonlight\_v1\smallskip

\noindent \textbf{Dokumente}\\
\indent AS726x\_Design\_Considerations.pdf\\
\indent AS7261\_Datasheet.pdf\\
\indent AS7265x\_Datasheet.pdf\\
\indent lTC4316-I2C-Translator\_Datasheet.pdf\\
\indent Program\_AS72xx\_FlashCatUSB.pdf\smallskip

\noindent \textbf{Hardware}\\
\indent Sensorboard\_Layout.pdf\\
\indent Sensorboard.brd\\
\indent Sensorboard.sch\\
\indent Status-Adapterboard\_Layout.pdf\\
\indent Status-Adapterboard.brd\\
\indent Status-Adapterboard.sch\smallskip

\noindent \textbf{Programmcode}\\
\indent default\_values.h\\
\indent Makefile\\
\indent lib\\
\indent \indent influxDB\_http\_Libary\\
\indent \indent \indent influxdb.c\\
\indent \indent \indent influxdb.h\\
\indent \indent wiringPi\_AS726X\_Libary\\
\indent \indent \indent AS726X.c\\
\indent \indent \indent AS726X.h\\
\indent src\\
\indent \indent main.c\\
\indent \indent measurement.c\\
\indent \indent measurement.h\\
\indent \indent welcome.c\\
\indent \indent welcome.h
\end{document}

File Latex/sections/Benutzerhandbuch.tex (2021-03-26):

\subsection{Hardware Setup}
Der Raspberry Pi muss mit seiner Stromversorgung (USB C), einem  Netzwerk (Ethernet) und 1-12 Sensorboards verbunden werden.
\subsection{Messung Starten}
Über das Terminal (Unter Windows cmd) muss eine SSH Verbindung zum Raspberry Pi aufgebaut werden.\\
\textbf{ssh pi@[IP-ADRESSE]}\\
Die Messsoftware befindet sich im Ordner $\sim$/SpectralSensor\\
\textbf{cd  $\sim$/SpectralSensor}\\
Damit die Messsoftware auch noch weiter läuft, wenn die SSH Verbindung wieder geschlossen wird, muss sie in einem Screen kompiliert werden.\\
\textbf{screen}\\
\textbf{make}\\
Um die SSH Verbindung zu trennen, ohne die Messung zu unterbrechen, wird einfach das Terminal/CMD Fenster geschlossen.\smallskip

\begin{figure}[H]
\centering

\caption{Terminal Output bei Start der Messsoftware }
\label{fig:Start-der-Messsoftware}
\end{figure}
\noindent Zuerst muss im Terminaloutput überprüft werden ob der NTP Server synchronisiert ist.
Wird eine falsche Systemzeit, angezeigt muss das Programm nach etwa 40 Sekunden neu Gestartet werden. Anschließend sollte die Systemzeit richtig sein. (Mehr zum Programm Neustart: \ref{restart}).\\
Im I2C Scann sollten alle angeschlossenen Sensoren angezeigt werden.\\
Die Messung wird mit den angezeigten Einstellungen gestartet, indem die Eingabeaufforderung mit \textbf{Y} bestätigt wird.\\
\begin{figure}[H]
\centering
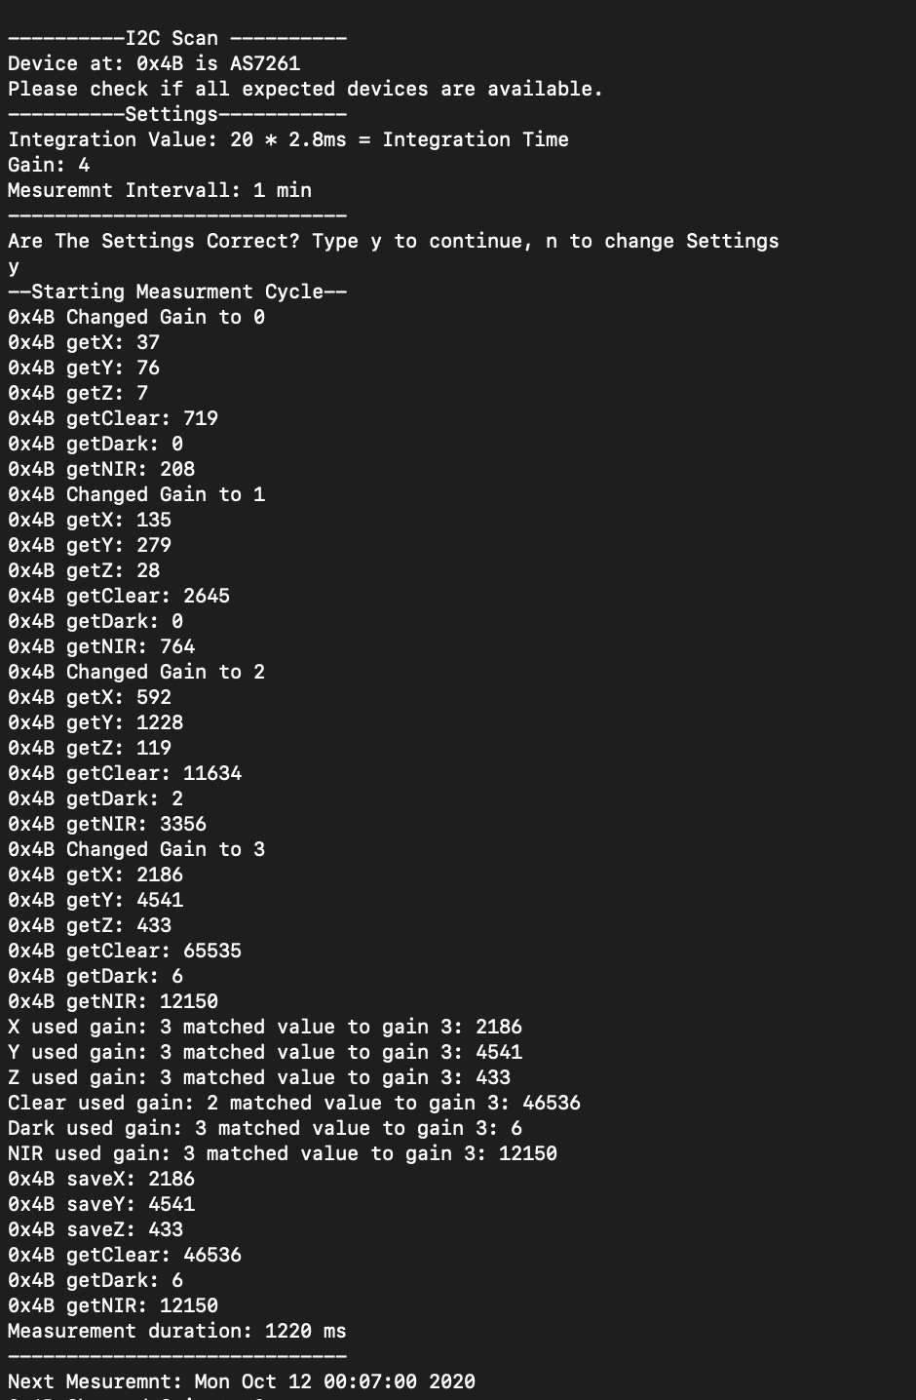
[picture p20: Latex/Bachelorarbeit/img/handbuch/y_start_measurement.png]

\caption{Terminal Output bei Start der Messung }
\label{fig:Start-der-Messung}
\end{figure}

Um die Einstellung zu verändern wird \textbf{N} ausgewählt.\\
\begin{figure}[H]
\centering
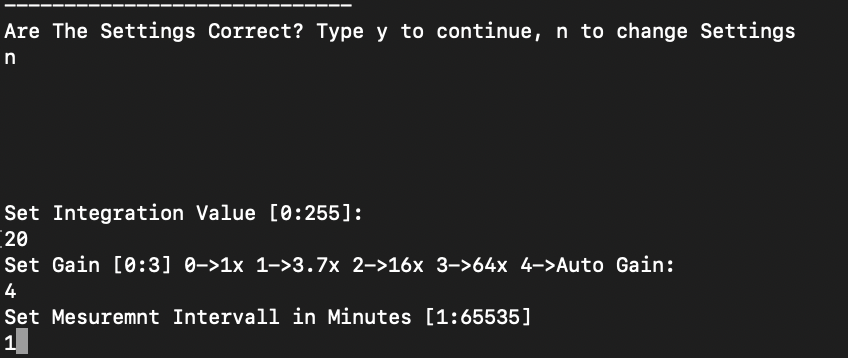
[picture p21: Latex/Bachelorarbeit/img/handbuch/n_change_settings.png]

\caption{Beispielhafter Terminal Output bei Einstellungsänderungen}
\label{fig:changesettings}
\end{figure}
\noindent Die Einstellungen werden nacheinander abgefragt, die Eingaben müssen mit Enter bestätigt werden.\medskip

\noindent Integration Value bestimmt die Integrationszeit, d. h. die Belichtungszeit der einzelnen Messungen.
Gain bestimmt den Verstärkungsfaktor der Messwerte. Im Auto Gain modus wird automatisch der am besten geeigneten Verstärkungsfaktor für jede einzelne Messung ausgewählt.
Measurement Interval ist das Intervall, in dem alle angeschlossenen Sensoren eine Messung durchführen.
\subsection{Einstellung für fortgeschrittene Benutzer}
 \begin{figure}[H]
\centering
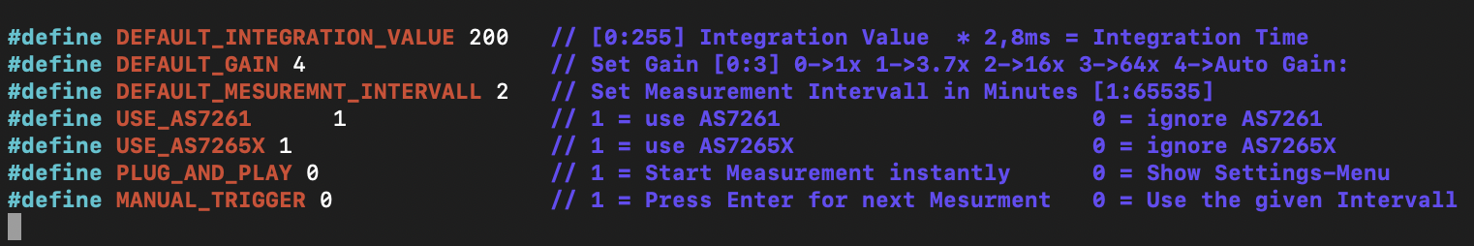
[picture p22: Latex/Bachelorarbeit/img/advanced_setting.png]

\caption{SpectralSensor/defaultvalues.h}
\label{fig:changesettings}
\end{figure}
 In der Datei \textbf{SpectralSensor/defaultvalues.h} können die beim Programmstart vorgeschlagenen Standardeinstellungen angepasst werden.\\
 Zusätzlich kann eingestellt werden, dass die Messung ohne manuelle Benutzerinteraktion direkt mit den Standardeinstellungen startet (PLUG\_AND\_PLAY).\\
 Um die Kalibrierung zu erleichtern, kann der automatische zeitbasierte Auslöser deaktiviert werden (MAUAL\_TRIGGER). Die einzelnen Messungen werden dann durch Drücken der Enter-Taste durchgeführt.

\subsection{Webinterface}
Das Grafana Webinterface ist unter folgender Adresse im Browser zu erreichen:\\
\textbf{[IP-ADRESSE]:3000}

\begin{figure}[H]
\centering
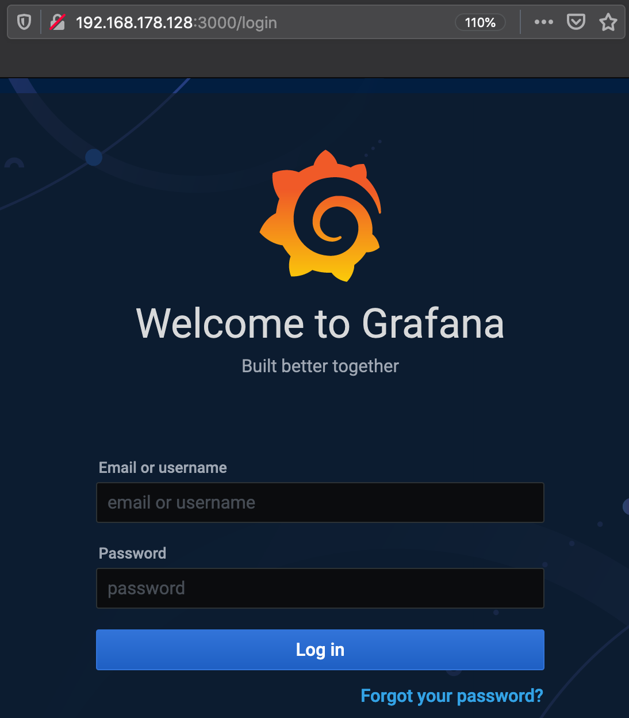
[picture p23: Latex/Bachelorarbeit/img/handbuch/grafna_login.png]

\caption{Grafana Login im Browser}
\label{fig:grafna_login}
\end{figure}
\noindent Im Example Dashboard sind alle Sensordatenplots vorhanden. Wenn weniger Plots benötigt werden oder die Darstellung angepasst werden muss, kann eine Kopie angefertigt und bearbeitet werden.\\
Um Daten im CSV-Format zu exportieren muss zuerst der gewünschte Zeitbereich ausgewählt werden.
Anschließend wird, wie in Abbildung \ref{fig:export_data} zu sehen, im Kontextmenü (Klick auf den Namen eines Plots) unter Inspect die Option Data ausgewählt. 

\begin{figure}[H]
\centering
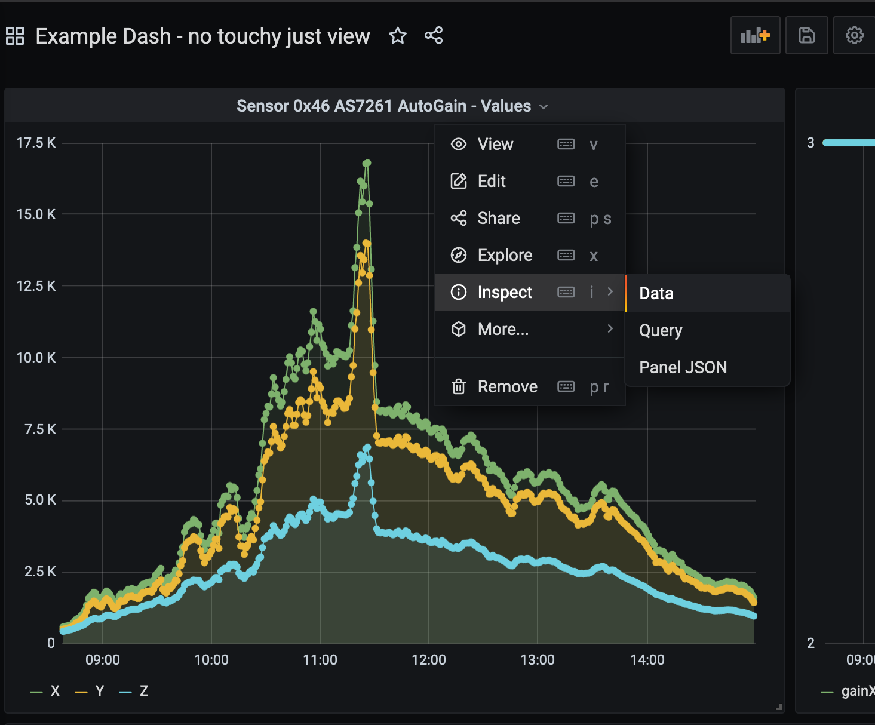
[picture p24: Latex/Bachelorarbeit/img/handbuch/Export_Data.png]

\caption{Screenshot Grafana CSV-Export}
\label{fig:export_data}
\end{figure}
\noindent Daten können nur pro Plot exportiert werden. Um mehr Daten auf einmal zu exportieren, müssen alle gewünschten Daten in einem Plot vereint werden.

\subsection{Messsoftware Beenden/Neustarten}
\label{restart}
Das Programm kann mit Control+C beendet werden.\\
Falls die SSH Verbindung geschlossen wurde, muss diese erst wieder aufgebaut werden.\\
\textbf{ssh pi@[IP-ADRESSE]}\\
Der Screen, in welchem die Messsoftware läuft, muss Attached sein.\\
\textbf{screen -r}\\
Die Liste aktiver Screens kann mit \textbf{screen -list} eingesehen werden.
Weiter Informationen zu Screen: \url{https://linuxize.com/post/how-to-use-linux-screen/}

\noindent Um die Software erneut zu starten, sollte sie wieder neu kompiliert werden, da so immer alle eventuellen Einstellungsänderungen in der Datei default\_values.h übernommen werden:\\
\textbf{cd ~./SpectralSensor}\\
\textbf{screen make}\\

\subsection{IP Adress Scan}
\paragraph{Unter Unix:} sudo nmap -sn 192.168.1.0/24  
\paragraph{Unter Windows:} Mit Hilfe der Software ''PortScan'' \\https://www.the-sz.com/products/portscan/\smallskip

\subsection{Bedeutung der Status LEDs}\label{leds}
\subsubsection{Rapsberry Pi}
Die rote PWR-LED leuchtet kontinuierlich bei stabiler 5V Stromversorgung.\\
Die grüne ACT-LED blinkt, wenn die SD-Karte korrekt arbeitet.
\subsubsection{Status \& Adapterboard}
Die rote Power-LED leuchtet, wenn eine Benutzereingabe zum Starten der Messungen erwartet wird.\\
Die grüne Heartbeat-LED leuchtet, wenn der Messzyklus gestartet wurde, geht aber immer während der eigentlichen Messung aus.
\subsubsection{Sensorboard}
Die roten LEDs D1-AS7261 und D2-AS7265X blinken, wenn es Probleme mit der Firmware auf dem Flaschenspeicher des jeweiligen Sensors gibt.

\subsection{Hilfe}
\textbf{Nach dem Starten der Messung gibt es keine Ausgabe in Terminal:}\\
Vermutlich sind keine Sensoren angeschlossen\\
\textbf{Die Systemzeit ist falsch:}\\
Keiner der NTP-Server aus der Liste /etc/systemd/timesyncd.conf kann erreicht werden.\\
\textbf{Das Webinterface ist nicht erreichbar:}\\
Entweder wurde die Adresse falsch geschrieben oder der Grafana-Server ist abgestürzt / wird nicht mehr automatisch gestartet.\\
\textbf{Error: 500
Write to Database Failed!:}
Der InfluxDB-Server ist abgestürzt / wird nicht mehr automatisch gestartet.
\subsection{Liste Der Verwendeten I2C Adressen \& Translationbytes}
\label{liste_Translationbytes}
Die Translation Bytes (Dezimal) 0- 59 wurden bereits verwendet. Sollten weitere Sensorboards angefertigt werden, muss es hier notiert werden:

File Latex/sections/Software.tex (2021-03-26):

Der Programmcode für den Messaufbau wurde in C geschrieben, da es einfach möglich ist, auf die GPIO des Raspberry Pi zuzugreifen. Im Übrigen ist die Sprache am Fachgebiet für Lichttechnik weitgehend geläufig.\\
Das folgende Kapitel ist in mehrere Punkte unterteilt. Zunächst werden die Funktionen der grundlegenden I2C Schnittstelle wiringPi Library vorgestellt (Abschnitt \ref{wiringPiI2CSetup}). Anschließend werden alle notwendigen Funktionen für die verwendeten AMS-Sensoren (Abschnitt \ref{AS726X-Library}) und die Schnittstelle zur Influx-Datenbank (Abschnitt \ref{AS726X-Library}) erläutert.
Abschließend wird der eigentliche Programmablauf aus der C-Datei main.c (Abschnitt \ref{main}) und measurement.c (Abschnitt \ref{measurement-c}) dargestellt.

\noindent Der Programmcode ist auf Github\footnote{\url{https://github.com/LennardBoediger/SpectralSensor}} und im Anhang zu finden.

\subsection{wiringPi}
Auf dem Rapberry Pi 4 ist die  wiringPi Libarry vorinstalliert. 
Die Funktionalität der drei verwendeten C-Funktionen wird im folgenden beschrieben.

\subsubsection{wiringPiI2CSetup}\label{wiringPiI2CSetup}
wiringPiI2CSetup baut eine I2C-Verbindung zu einem Slave-Gerät auf.
Der Funktion wird beim Aufruf die I2C Adresse übergeben, mit welcher eine Verbindung aufgebaut werden soll: $wiringPiI2CSetup(address)$.\\
Der Rückgabewert ist der Standard Linux File Descriptor oder -1, falls ein Fehler auftritt. 
Der File Descriptor wird im Programmcode mit fd abgekürzt.
Ein File Descriptor wird unter Linux als Bezeichner für eine Datei bzw. eine andere Ein-/Ausgabe-Ressource wie z. B. eine Pipe, einen Network-Socket oder eine I2C Verbindung genutzt.

Die Anzahl der File Desciptoren ist begrenzt. Daher muss die Verbindung mit der Funktion $close()$ aus der Library: unistd.h geschlossen werden, wenn sie nicht mehr benötigt wird.

\subsubsection{wiringPiI2CWriteReg8}
wiringPiI2CWriteReg8 überträgt ein Byte an einen I2C-Slave.
Der Funktion wird beim Aufruf der File Descriptor einer aktiven I2C-Verbindung sowie ein Zielregister und die zu schreibenden 8bit Daten übergeben:\\ $wiringPiI2CWriteReg8 (fd, RegAdr, 8BitData)$.\\
Wenn der Schreibzugriff vom I2C-Slave bestätigt wurde, wird eine 0 zurückgegeben.

\subsubsection{wiringPi4I2CReadReg8}
wiringPi4I2CReadReg8 überträgt ein Byte an einen I2C-Slave.
Der Funktion wird beim Aufruf der File Descriptor einer aktiven I2C Verbindung sowie ein Zielregister übergeben: $wiringPiI2CReadReg8(fd, RegAdr)$.\\
Der gelesene 8-Bit-Inhalt des Registers ist der Rückgabewert.
Wenn das Lesen fehlschlägt, bleibt das Programm in einer Endlosschleife hängen.

\subsection{AS726X Library}\label{AS726X-Library}
Die WiringPi\_AS726X\_Libary enthält alle Funktionen um den AS7261 und AS7265X zu steuern und auszulesen.
Da der Beispielcode und die sonstigen Angaben im Datenblatt in vielen Detailfragen ungenau und Fehlerhaft sind, wurde die Arduino OpenSource Libarrys von sparkfun SparkFun\_AS726X\_Arduino\_Library-master und SparkFun\_AS7265x\_Arduino\_Library als Implementierungsgrundlage verwendet.
Im ersten Schritt der Entwicklung wurde sie für die I2C Schnittstelle, wiringPi Libarry des Rapberry Pi 4 umgeschrieben und anschließend in ihrer Funktionalität erweitert, um für das Messystem mit mehreren Sensoren auf dem gleichen I2C-Bus nutzbar zu sein. \\

\noindent Im Folgenden Text werden die Registeradressen mit den gleichen Namen wie im Programmcode bezeichnet. Die numerischen Adressen sowie ihre Aufgaben sind in den Abbildungen \ref{fig:PysicalRegister}-\ref{fig:AS7265X_DEV_SELECT_CONTROL} zu finden.

\begin{figure}[H]
\centering
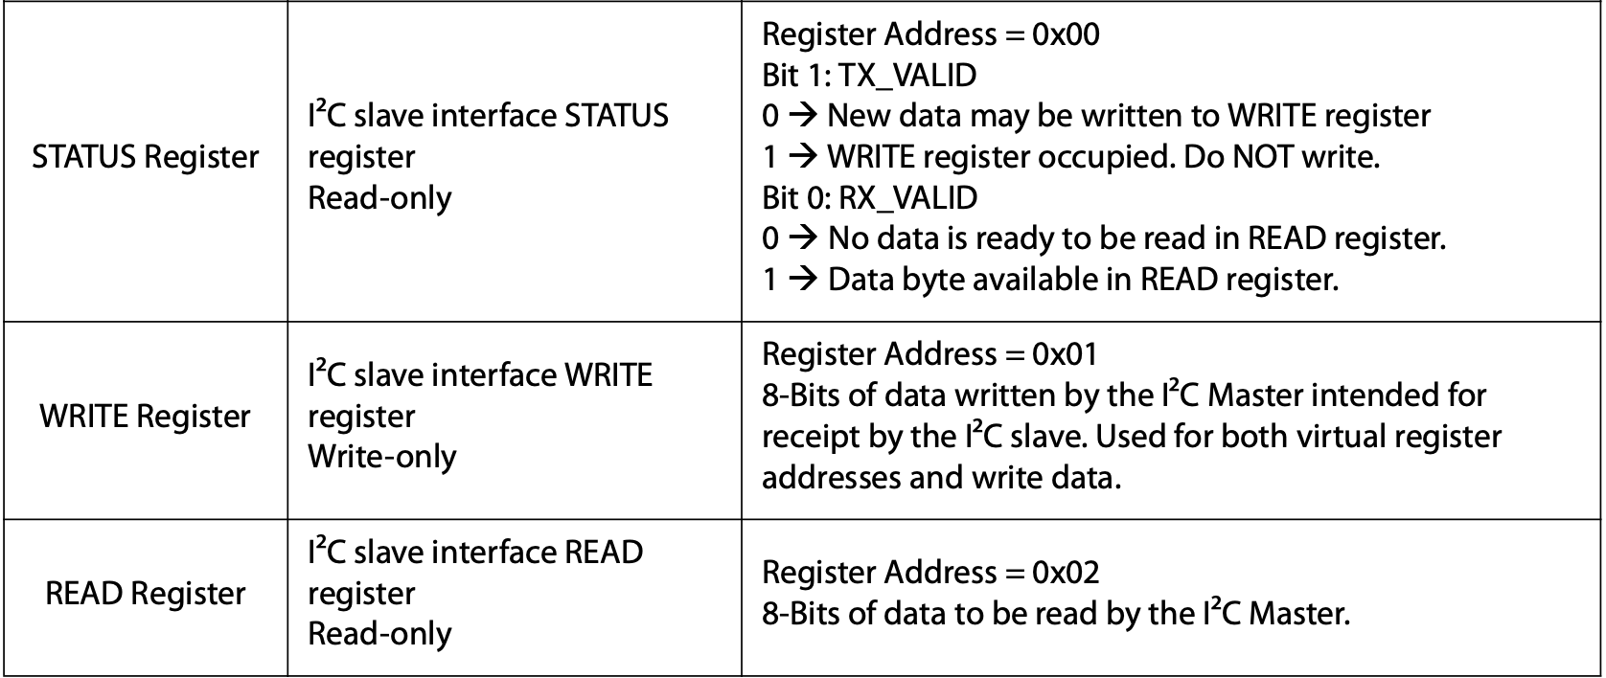
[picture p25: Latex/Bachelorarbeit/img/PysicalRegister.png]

%\caption*{Quelle: Datenblatt AS7261}
\caption{PysicalRegister\cite{Datenblatt_AS7261}}
\label{fig:PysicalRegister}
\end{figure}

\begin{figure}[H]
\centering
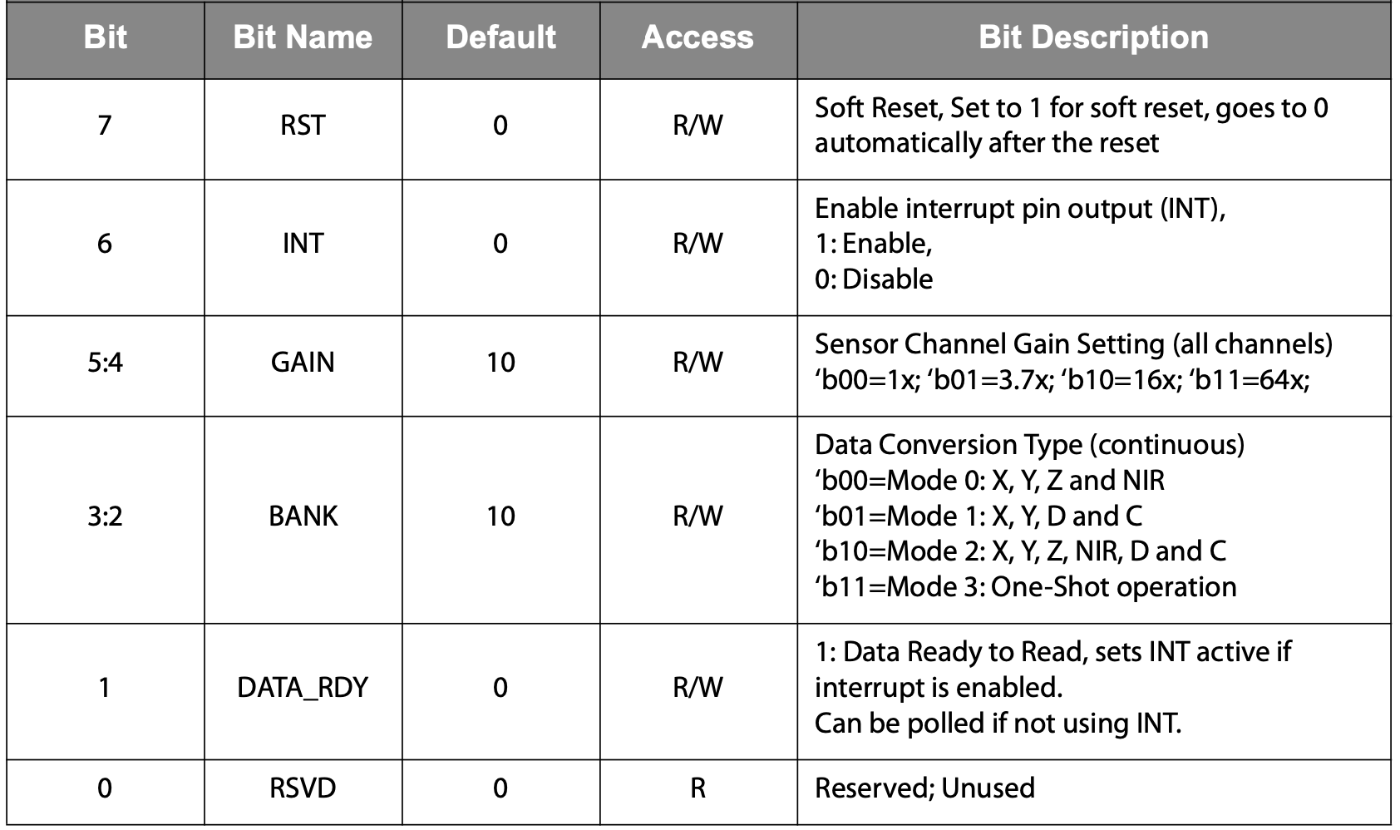
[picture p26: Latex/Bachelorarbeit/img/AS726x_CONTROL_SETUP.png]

\caption{AS726x\_CONTROL\_SETUP 0x04\cite{Datenblatt_AS7261}}
\label{fig:AS726x_CONTROL_SETUP}
\end{figure}

\begin{figure}[H]
\centering

\caption{AS726x\_INT\_T 0x05\cite{Datenblatt_AS7261}}
\label{fig:AS726x_INT_T}
\end{figure}

\begin{figure}[H]
\centering

\caption{AS726x\_DEVICE\_TEMP 0x06\cite{Datenblatt_AS7261}}
\label{fig:AS726x_DEVICE_TEMP}
\end{figure}

\begin{figure}[H]
\centering
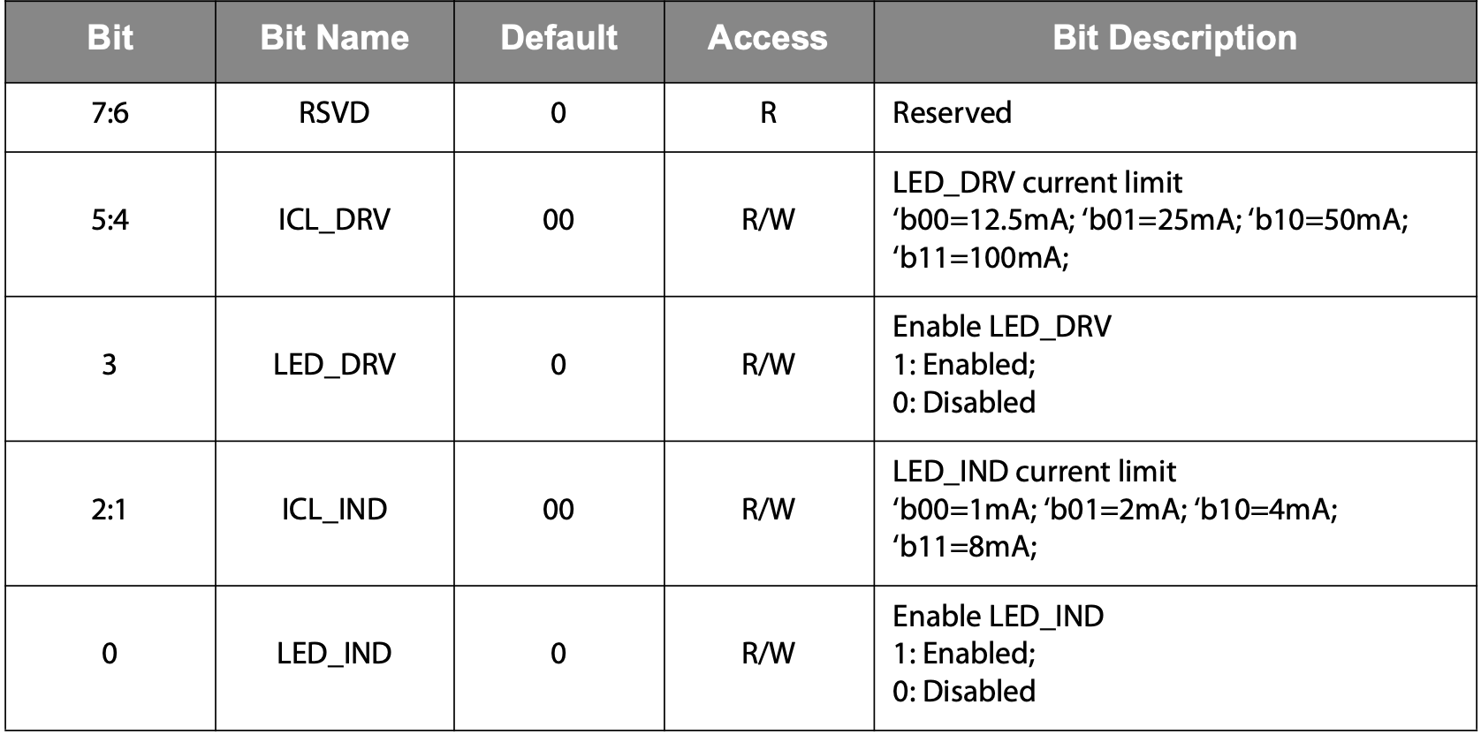
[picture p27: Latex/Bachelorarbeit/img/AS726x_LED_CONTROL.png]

\caption{AS726x\_LED\_CONTROL 0x07\cite{Datenblatt_AS7261}}
\label{fig:AS726x_LED_CONTROL}
\end{figure}

\begin{figure}[H]
\centering
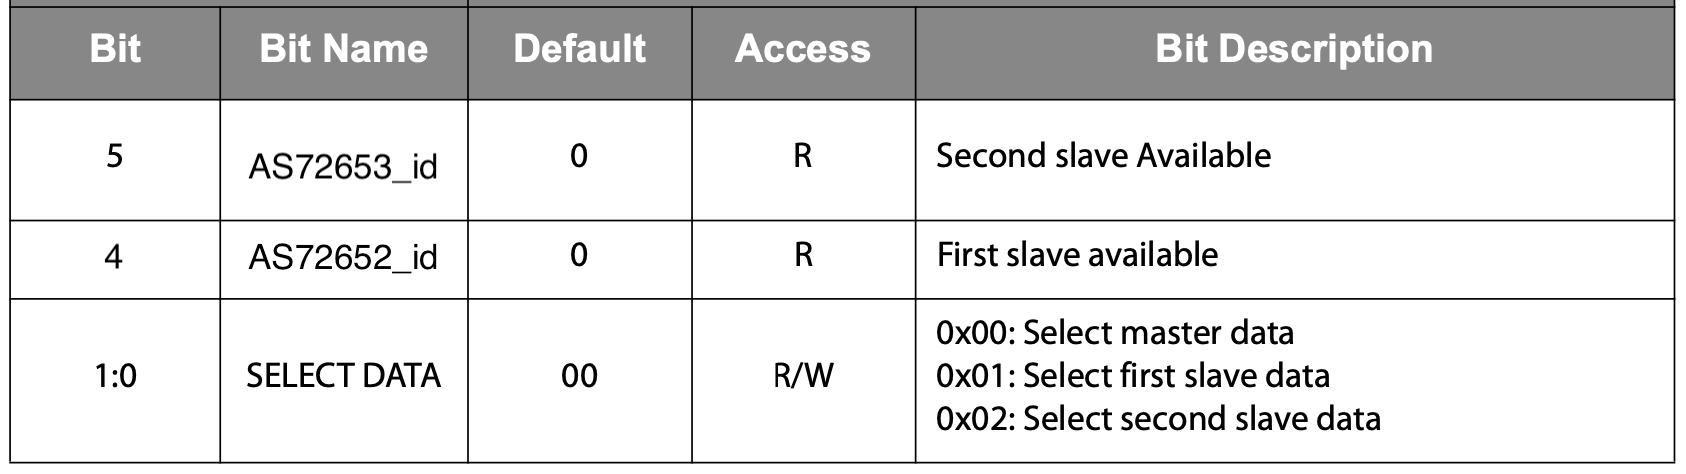
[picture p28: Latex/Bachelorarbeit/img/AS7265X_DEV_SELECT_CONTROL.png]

\caption{AS7265X\_DEV\_SELECT\_CONTROL 0x4F\cite{Datenblatt_AS7261}}

\label{fig:AS7265X_DEV_SELECT_CONTROL}
\end{figure}

\begin{table}[!ht]
\centering
\caption{Raw Data Registers \cite{Datenblatt_AS7261}}
\begin{tabular}{ l r }
 Name & Adresse\\ 
AS7261\_X & 0x08\\
AS7261\_Y & 0x0A\\
AS7261\_Z & 0x0C\\
AS7261\_NIR & 0x0E\\
AS7261\_DARK & 0x10\\
AS7261\_CLEAR & 0x12\\
AS7265X\_R\_G\_A & 0x08 \\
AS7265X\_S\_H\_B & 0x0A \\
AS7265X\_T\_I\_C & 0x0C \\
AS7265X\_U\_J\_D & 0x0E \\
AS7265X\_V\_K\_E & 0x10 \\
AS7265X\_W\_L\_F & 0x12 \\
\end{tabular}
\label{fig:raw_channel_registers}
\end{table}

\subsubsection{virtualWriteRegister}
Wie bei Embedded-Geräten üblich, werden Einstellungen auf dem Sensor verändert, indem verschiedene sogenannte Special Function Register mit Daten beschrieben werden.\\
Jedes Special Function Register ist 8Bit groß und hat eine Adresse. Jedes Bit des Registers repräsentiert eine Einstellung.
Beispielsweise ist 0x07 (Abbildung \ref{fig:AS726x_LED_CONTROL}) das LED Control Register des Sensors.
Bit 0 des Registers beschreibt den Zustand der Status LED.
Die Restlichen 7 Bit des Registers beschreiben den Zustand anderer LEDs, die für den Messaufbau aber irrelevant sind.\\
Wird Register 7 mit dem Dezimalwert 0 beschrieben sind alle LEDs aus. Wird es mit dem Dezimalwert 1 beschrieben, leuchtet nur die Status LED.
Die Register lassen sich aber nicht direkt beschreiben. Stattdessen sind sie als sogenannte virtuelle Register implementiert.
Das heißt, dass nur Register 0x01 (WRITE Register Abbildung \ref{fig:PysicalRegister}) beschrieben werden kann.
Um Daten in eines der Special Funktion Register zu schreiben, wird die C-Funktion virtualWriteRegister verwendet.
Die Funktionsweise lässt sich in 4 Schritten zusammenfassen:
\begin{itemize}
	\item Zeile 8 wartet, bis das WRITE Register leer ist. Was dadurch angezeigt wird, indem  das Bit AS72XX\_TX\_VALID im  Register AS72XX\_STATUS\_REG den Wert 1 annimmt.
	\item Zeile 14 schreibt die virtuelle Adresse in das WRITE Register und setzt zusätzlich Bit 8 des WRITE Register auf 1, um zu zeigen, dass es sich um einen schreibenden Zugriff auf das virtuelle Register handelt.
	\item Zeile 20 wartet erneut bis das WRITE Register leer ist.
	\item Zeile 26 schreibt die Daten in das WRITE Register
\end{itemize}
Der Sensor wird jetzt selber die übertragenen Daten aus dem WRITE Register in das angegebene virtuelle Register kopieren.
\lstinputlisting[language=C,style=c]{code/virtualWriteRegister.c}

\subsubsection{virtualReadRegister}
Die Unterschiedlichen Messdaten des Sensors werden in dedizierten Registern gespeichert.
 Es ist aber nur über den indirekten Weg des AS72XX\_READ\_REG und der virtuellen Registeradressen möglich Daten auszulesen.
Die Funktionsweise der zum Datenauslesen benötigten Funktion virtualReadRegister lässt sich wieder in 4 Schritte aufteilen.
\begin{itemize}
	\item Das AS72XX\_READ\_REG wird ausgelesen, ohne dass die Daten verarbeitet werden. Dieser Schritt ist wie ein Reset des Registers zu verstehen.
	\item Zeile 12 schreibt die virtuelle Adresse in das WRITE Register und setzt zusätzlich Bit 8 des WRITE Register auf 0 um zu zeigen, dass es sich um einen Lesendezugriff auf das virtuelle Register handelt.
	\item Sobald das AS72XX\_STATUS\_REG den Wert AS72XX\_TX\_VALID annimmt, sind die Daten aus dem angegebenen virtuellen Register in das AS72XX\_READ\_REG kopiert worden.
	\item Zeile 28 liest die Daten aus dem S72XX\_READ\_REG
\end{itemize}
\lstinputlisting[language=C,style=c]{code/virtualReadRegister.c}

\subsubsection{MeasurementFromAdress}
Die Funktion baut eine I2C Verbindung zur übergebenen Bus-Adresse auf und  ruft die Funktion takeMeasurments mit dem File Descriptor der aktiven I2C Verbindung auf.
Nachdem die Funktion takeMeasurements durchgelaufen ist, wird die I2C Verbindung wieder geschlossen.
\lstinputlisting[language=C,style=c]{code/MeasurementFromAdress.c}

\subsubsection{takeMeasurements}

Die Funktion takeMeasurements ruft die Funktion setMeasurementMode mit dem Parameter 3 auf. Das setzt den aus \ref{sec_bank_modes} bekannten Bank Mode der übergebenen I2C Verbindung auf Bank Mode 3.
	Die One-Shot Messung wird sofort gestartet. In Zeile 9 wird gewartet, bis die Messung abgeschlossen ist. 
		Um sicherzustellen, dass die Funktion DataAvailable richtig arbeitet, muss vor der Messung das Flag DataAvailable auf 0 gesetzt werden (Zeile 3).
Die Daten werden hier nicht ausgelesen, daher gibt es keinen Rückgabewert.\\
\lstinputlisting[language=C,style=c]{code/takeMeasurements.c}

\subsubsection{setMeasurementMode}
Mit der Funktion setMeasurementMode werden die Bank Mode Bits 2 und 3 des \\
AS726x\_CONTROL\_SETUP Registers mit dem gewünschten Wert für den Bank Mode beschrieben.\\
Da die anderen Bits des Registers noch weitere Einstellungen repräsentieren, welche nicht verändert werden sollen, muss das Register erst ausgelesen werden.
Anschließend werden nur die Bank Mode Bits auf 0 gesetzt, um im nächsten Schritt mit dem gewünschten neuen Bank Modewert beschrieben zu werden. 
Die Bedeutung der Bank Modes ist in \ref{sec_bank_modes} erläutert.
\lstinputlisting[language=C,style=c]{code/setMeasurementMode.c}
\newpage
\subsubsection{dataAvailable \& clearDataAvailable}
Das Bit dataAvailble im Register AS726x\_Control\_Setup wird vom Sensor auf 1 gesetzt, wenn nach einer Messung neue Daten vorhanden sind. Interrupts müssen dafür ausgeschaltet sein.
Wenn eine One-Shot Messung im Bank Mode 3 durchgeführt wird, muss das dataAvailble Bit mit der Funktion clearDataAvailable auf 0 gesetzt werden. Die Funktion dataAvailable gibt den Wert des DataAvailable Bit zurück.\\

%\lstinputlisting[language=C,style=c]{code/dataAvailable.c}

\subsubsection{Rohwerte des AS7261 auslesen}
Die in Abschnitt \ref{sec_bank_modes} beschrieben 6 Channel des AS7261 werden mit den folgenden Funktionen ausgelesen:
\begin{itemize}
	\item getX\_CIE(fd)
	\item getY\_CIE(fd)
	\item getZ\_CIE(fd)
	\item getNIR(fd)
	\item getDark(fd) 
	\item getClear(fd)
\end{itemize}
Der File Deskriptor einer I2C Verbindung mit einem AS7261 und das zu lesende Register (Abbildung \ref{fig:raw_channel_registers}) wird als Übergabeparameter erwartet.\\
Um den Messwert auszulesen, wir die Funktion getchannel aufgerufen.
Der Rückgabewert ist der 16-Bit Messwert aus dem jeweiligen Register vom Datentyp Integer.
\lstinputlisting[language=C,style=c]{code/getRaw_AS7261.c}

\subsubsection{getChannel}
Da die Messdaten 16 Bit groß sind, der Sensor aber nur über 8 Bit Register verfügt, werden 2 aufeinader folgende Register ausgelsen und im Big-Endian Format in einer 16 Bit Variable gespeichert .
Die Funktion getChannel erwartet den File Descriptor einer I2C Verbindung zu einem Sensor und die Adressen des High Bytes eines Raw Data Registers.
Der Rückgabewert ist der 16-Bit Messwert aus dem jeweiligen Register vom Datentyp Integer.\\

\lstinputlisting[language=C,style=c]{code/getChannel.c}

\subsubsection{Rohwerte des AS7265X auslesen}\label{Rohwerte-des-AS7265X-Auslesen}
Da beim Lesen des AS7265X, 3 Sensoren unter der gleichen Adresse erreichbar sind (Abbildung \ref{fig:raw_channel_registers}), muss zusätzlich zum File Descriptor und des Zielregisters der Device Identifier angeben werden.
Die folgenden Funktionen übernehmen diese Aufgaben und können genutzt werden, um Rohdaten auslesen:
\begin{center}
\begin{tabular}{ c c c }
 	AS72651 & AS72652 & AS72653 \\ 
 	getR(fd) & getG(fd) & getA(fd) \\  
 	getS(fd) & getX(fd) & getB(fd) \\
 	getT(fd) & getI(fd) & getC(fd) \\  
 	getU(fd) & getJ(fd) & getD(fd) \\
 	getV(fd) & getK(fd) & getE(fd) \\  
 	getW(fd) & getL(fd) & getF(fd) \\
\end{tabular}
\end{center}
Um den Messwert auszulesen, wir die Funktion getChannel\_AS7265X aufgerufen.\\
Der Rückgabewert ist der 16-Bit Messwert aus dem jeweiligen Register vom Datentyp Integer.\\

%\lstinputlisting[language=C,style=c]{code/getRaw_AS7265X.c}

\subsubsection{getChannel\_AS7265X}\label{getChannel_AS7265X}
Die Funktion verarbeitet den aus Abschnitt \ref{Rohwerte-des-AS7265X-Auslesen} bekannten Device Identifier, indem die Funktion selectDevice aufgerufen wird.
	Da es aber keine Möglichkeit gibt zu überprüfen ob der Gerätewechsel erfolgreich war, muss vorher überprüft werden ob das jeweiligen Slavegerät AS72652 oder AS72653 vorhanden ist.
	Ist ein Slave nicht vorhanden, wird der Wert -1 zurückgegeben.
	Ohne diese Überprüfung ist nicht sichergestellt, dass keine falschen Werte aus den gleich nummerierten Registern des AS72651 ausgelesen werden, obwohl Werte eines nicht vorhanden oder falsch aufgelöteten Slavesensors (AS72652 / AS72653) erwartet werden.
	Das eigentliche Auslesen des 16-Bit Messwerts erfolgt mithilfe der Funktion getChannel, das Ergebnis ist der Rückgabewert der Funktion getChannel\_AS7265X.\\

\lstinputlisting[language=C,style=c]{code/getChannel_AS7265X.c}
\newpage
\subsubsection{selectDevice}
Die Notwendigkeit für selectDevice wurde in Abschnitt \ref{getChannel_AS7265X} bereits erläutert.
Laut Datenblatt sollen nur die Bits 0 und 1 des DEV\_SELECT\_CONTROL Registers beschrieben werden, das stimmt aber nicht.\\
In der Realität muss das gesamte 8-bit Register mit folgenden Werten beschrieben werden um beim anschließenden Lesevorgang Daten vom jeweiligen Sensor zu erhalten.
\begin{center}
\begin{tabular}{ c c }
 	DEV\_SELECT\_CONTROL & Sensor \\ 
 	0x00 & AS72651 \\  
 	0x01 & AS72652 \\
 	0x02 & AS72653 \\  
\end{tabular}
\end{center}

\lstinputlisting[language=C,style=c]{code/selectDevice.c}

\subsubsection{Enable/Disable Indicator}
Mit der Funktion enableIndicator wird das 0 Bit des AS726x\_LED\_CONTROL Register auf 1 gesetzt. So wird die rote Status LED des jeweiligen Sensors auf dem Sensorboard angeschaltet.\\
Mit der Funktion disableIndicator wird das gleiche Bit auf 0 gesetzt, also die LED ausgeschaltet.\\
Als Übergabeparameter wird bei beiden Funktionen der File Descriptor einer aktiven I2C-Verbindung erwartet.\\

%\lstinputlisting[language=C,style=c]{code/enableIndicator.c}

\subsubsection{softReset}
Wenn einzelne Messwerte außerhalb des Erwartungsbereichs liegen oder ähnliche Probleme auftreten, kann in einigen Fällen ein Soft-Reset das Problem beheben.
Da bei der hier beschriebenen Implementierung keine Fehler auftreten, wird die Funktion nicht benötigt, kann aber in zukünftigen Versionen verwendet werden.

\noindent Die Funktion softReset setzt das 8 Bit des Registers CONTROL\_SETUP auf 1 um einen softReset auszulösen.
Das Datenblatt gibt an, dass mindestens 1000 ms gewartet werden muss, bevor der softReset abgeschlossen ist und der Sensor wieder genutzt werden kann.
Für beide Funktionen wird der File Descriptor einer aktiven I2C-Verbindung als Übertragungsparameter erwartet.\\

%\lstinputlisting[language=C,style=c]{code/softReset.c}

\subsubsection{I2CScan}
Die Funktion I2CScan wird zu Beginn des Programms aufgerufen um festzustellen, welche Sensoren an den I2C DataBus angeschlossen sind.
Die gefundenen Sensoradressen und der Sensortyp werden in das Struct sensor\_list geschrieben.\\
Die Adressen werden außerdem im Terminal angezeigt, so dass der Benutzer überprüfen kann, ob alle erwarteten Sensoren erkannt werden.
Als Übergabeparameter wird im call by refrence style ein Pointer zu einem Struct vom Typ sensor\_list erwartet.
Da die Daten direkt in das extern deklarierte Struct geschrieben werden, gibt es keinen Rückgabewert.
Um die angeschlossenen Sensoren zu detektieren, wird zu jeder der $2^8$ möglichen I2C Adressen eine Verbindung aufgebaut und ein Schreibversuch mithilfe der Funktion wiringPiI2CWriteReg8 vorgenommen.
Wenn die Funktion wiringPiI2CWriteReg8 eine 0 zurückgibt, war der Schreibversuch erfolgreich. Somit muss ein Sensor unter dieser Adresse vorhanden sein.
Das im Datenblatt nicht erwähnte Register mit der Adresse 0x05 wurde zufällig ausgewählt, da es mit dem Wert 0x01 beschrieben werden kann, ohne dass der Sensor sein Verhalten verändert.
Die Funktion getVersion wird genutzt um die Version des gefunden Sensors zu ermitteln.
Wenn ein AS72651 erkannt wird, wird auch abgefragt, ob die Slavesensoren AS72652 und AS72653 vorhanden sind. Diese Information wird nur im Terminal ausgegeben und nicht in das Struct sensor\_list geschrieben, da es für den Programmablauf nicht notwendig ist.\\

\lstinputlisting[language=C,style=c]{code/I2C_Scan.c}

\subsubsection{getVersion}
Die Funktion getVersion gibt den Inhalt der Registers AS726x\_HW\_VERSION zurück. Indem der zurückgegebene Wert mit den beiden SENSORTYPE Werten verglichen wird (SENSORTYPE\_AS7261 und SENSORTYPE\_AS72651), kann festgestellt werden, um welchen Sensor es sich handelt. 
Als Übergabeparameter wird bei beiden Funktionen der File Descriptor einer aktiven I2C-Verbindung erwartet.

\subsubsection{scanAS7262}
Als Übergabeparameter wird bei der Funktionen der File Descriptor einer aktiven I2C Verbindung mit einem AS72651 erwartet.\\
Die Funktion überprüft den Status des 4. Bit des Registers DEV\_SELECT\_CONTROL und gibt ihn zurück. Das Bit ist auf 1 gesetzt, wenn der Slavesensor AS7262 vorhanden ist, im Falle der Abwesenheit ist es 0.\\
Das AS7265X-Datenblatt gibt fälschlicherweise an, dass das 5. Bit geprüft werden muss.\\

\subsubsection{scanAS7263}
Als Übergabeparameter wird bei der Funktionen der File Descriptor einer aktiven I2C Verbindung mit einem AS72651 erwartet.\\
Die Funktion überprüft den Status des 5. Bit des Registers DEV\_SELECT\_CONTROL und gibt ihn zurück. Das Bit ist auf 1 gesetzt wenn der Slavesensor AS7263 vorhanden ist, im falle der Abwesenheit ist es 0.\\

\subsubsection{setGain}
Die Messergebnisse der Sensoren können intern verstärkt werden, was Beispielsweise in dunklen Messumgebungen oder bei der Verwendung einer relativ lichtundurchlässiger Streuscheibe notwendig ist.\\
Außerdem kann das Speicherregister besser ausgesteuert werden, um ein genaueres Messergebnis zu erhalten.
Um den Verstärkungsfaktor einzustellen, wird die Funktion setGain benötigt.\\
Die Funktion setGain beschreibt das vierte und fünfte Bit des Registers CONTROL\_SETUP mit einem der vier möglichen Zustände, welcher an die Funktion übergebenen wird.

\begin{tabular}{ l l}
 	Wert & Verstärkungsfaktor \\ 
 	0 & 1x \\  
 	1 & 3.7x \\
 	2 & 16x \\  
 	3 & 64x \\
\end{tabular}

Ist der übergebe Wert größer als 3, wird das Register auf den Wert 3 gesetzt.
\begin{equation}
	Registerwert = Integrierter Messwert \cdot Gain
\end{equation}

\subsubsection{setIntegrationTime}
Um die Integrationszeit der Messung einzustellen, wird in das Register AS726x\_INT\_T ein Wert (integrationValue) zwischen 0 und 255 geschrieben. Die Integrationszeit errechnet sich indem dieser Wert mit dem Faktor 2.8ms multipliziert wird.
Die Funktion setIntegrationTime erwartet als Übergabeparameter das integrationValue und den File Descriptor sowie eine aktive I2C-Verbindung zu einem Sensor.\\
\begin{equation}
	Integrationszeit = integrationValue\cdot2.8ms
\end{equation}

\subsubsection{disableInterrupt}
Die Funktion disableInterrupt setzt das INT Bit im Register AS726x\_CONTROL\_SETUP auf 0 um Interrupts auszuschalten.
Da der Interrupt-Pin auf der Sensor-Platine nicht angeschlossen ist, können Messungen nur durchgeführt werden, wenn der Interrupt ausgeschaltet ist.
Laut Datenblatt wird der Interrupt beim Systemstart ausgeschaltet.

\subsection{influxDB Library writeToDatabase}\label{influxDB-Library}
Um die Messdaten der Sensoren in die aus \ref{datenbankundinterface} bekannte InfluxDB zu schreiben, wurde die InfluxDB Library entwickelt. Sie enthält nur eine einzige nach außen sichtbare Funktion: writeToDatabase.
\subsubsection{writeToDatabase}
Um die Datenbank zu beschreiben, muss zuerst ein Socket geöffnet werden um sich mit der InfluxDB Server-Instanz  zu verbinden.
Der InfluxDB Sever ist unter der Localhostaddress 127.0.0.1 am Port 8086 zu erreichen.
	Diese Werte können in der influxdb.h Datei angepasst werden, falls in Zukunft die Notwendigkeit besteht, den Server auf einem externen Gerät zu betreiben.\\
Die Kommunikation mit dem InfluxDB Server erfolgt über das HTTP basierte InfluxDB-Line-Protocol.
In Zeile 68 wird der Datenbankname, Username,  Passwort der Datenbank und die Größe des Bodys der Anfrage in den Header-Teil der HTTP Anfrage geschrieben.
In Zeile 64 wird der Body-Teil der Anfrage im InfluxDB-Line-Protocol Format erzeugt. Dieser enthält den Bezeichner des Messwerts (z.B. X oder Y), die I2C Adresse des jeweiligen Sensors von dem die Messdaten stammen, den Messwert selbst sowie den Zeitstempel der Messung in ms.	
In Zeile 85 wird der HTTP-Request, bestehend aus Header und Body, an den Server übertragen.
Die Antwort vom Server wird gespeichert und anschließen auf die erwartete Rückmeldung \textbf{HTTP/1.1 204 No Content } untersucht. Wenn der Schreibversuch fehlschlägt, wird eine Meldung im Terminal angezeigt.
Außerdem geht die Power-LED auf dem Status \& Adapterboard aus.
\subsection{main}\label{main}
Die main-Funktion führt den Benutzer durch den Auswahlprozess der Einstellungen (Integrationszeit, Verstärkungsfaktor und Intervall der Messpunkte) und startet dann die Messung.\\
\subsubsection{default\_values.h}
\noindent Alternativ zum Auswahlprozess können die Einstellungen in der Datei default\_values.h geändert werden. Hier ist es außerdem möglich, den zu verwendenden Sensortyp auszuwählen und die benutzerfreundliche Menüführung auszuschalten(Plug-and-Play).
Zudem kann eingestellt werden, dass die Messungen manuell auslöst werden, z. B. um den Sensor zu kalibrieren (Maunual-Trigger).\\

\lstinputlisting[language=C,style=c]{code/default_values.h}
\newpage
\subsection{measurement}\label{measurement-c}
Die Datei measurement.c enthält alle Funktionen, die mithilfe der beiden Libraries (influxDB Library \ref{influxDB-Library}, AS726X Library \ref{AS726X-Library}), Messergebnisse von den Sensoren abfragen und in der Datenbank speichern können.

\subsubsection{fixedGainMeasurementAS7261 \& fixedGainMeasurementAS7265X}
Bei der Messung mit konstanter Verstärkung werden alle Werte mit einer festen Integrationszeit und einem festen Gain erfasst. Es gibt also für jeden Kanal einen Wert, der unter dem gleichen Namen gespeichert wird. In der Datenbank sind sie unter den in Tabelle \ref{fix_Datenbankname_61} und \ref{fix_Datenbankname_65} beschriebenen Namen zu finden.

\begin{table}[H]
\parbox{.45\linewidth}{
\centering
\begin{tabular}{ c }
Fixed Gain \\
\hline
X \\ 
Y  \\
Z  \\
Clear \\ 
Dark \\ 
NIR \\ 
\end{tabular}
\caption{AS7261 Datenbank-ID bei festem Verstärkungsfaktor}
\label{fix_Datenbankname_61}

}
\hfill
\parbox{.45\linewidth}{
\centering
\begin{tabular}{ r c l}
&Fixed Gain \\
\hline
 	R & G & A \\  
 	S & X & B \\
 	T & I & C \\  
 	U & J & D \\
 	V & K & E \\  
 	W & L & F \\

\end{tabular}
\caption{AS7265X Datenbank-ID bei festem Verstärkungsfaktor}
\label{fix_Datenbankname_65}
}
\end{table}

\noindent Das Flussdiagramm in Abbildung \ref{fig:manualGain} beschreibt den Ablauf für fixedGainMeasurementAS7261.
Der Ablauf von fixedGainMeasurementAS7265X ist bis auf den SENSORTYP und die Namen der Channel identisch.

\begin{figure}[H]
  \centering
    \caption{Flowchart fixedGainMeasurementAS7261}
 
  \label{fig:manualGain}
\end{figure}

\subsubsection{autoGainMeasurementAS7261 \& autoGainMeasurementAS7265X}
Bei der Auto-Gain-Messung wird für jeden der 4 möglichen Verstärkungsfaktoren eine Messung mit fester Integrationszeit durchgeführt.
Die Messergebnisse werden in der Datenbank unter den in Tabelle \ref{auto_Datenbankname} und \ref{auto_Datenbankname_AS7265X} beschriebenen Namen gespeichert.
Darüber hinaus wird bei jeder einzelnen Messung für jeden Channel individuell der Messwert ausgewählt, welcher das 16 Bit Register am besten aussteuert.
Dieser Wert wird mit der Funktion matchValueToMaxGain (Abschnitt \ref{matchValueToMaxGain}) an die maximale Verstärkung angepasst um einen sprungfreien Output-Plot zu ermöglichen (Datenbank-ID AutoGain).
Zuletzt wird der verarbeitete Wert und der ursprünglich verwendete Gain in der Datenbank gespeichert.

\begin{table}[H]
\centering
\begin{tabular}{ c c c c c c}
Gain 0 & Gain 1 & Gain 2 & Gain 3 &  AutoGain & UsedGain \\
\hline
X*0 & X*1 & X*2 & X*3 & X & gainX  \\ 
Y*0 & Y*1 & Y*2 & Y*3 &  Y & gainY  \\
Z*0 & Z*1 & Z*2 & Z*3 &  Z & gainZ  \\
Clear*0 & Clear*1 & Clear*2 & Clear*3 & Clear & gainClear \\ 
Dark*0 & Dark*1 & Dark*2 & Dark*3 &  Dark & gainDark \\ 
NIR*0 & NIR*1 & NIR*2 & NIR*3 &  NIR & gainNIR  \\ 
\end{tabular}
\caption{AS7261 Datenbank-ID bei automatischem Verstärkungsfaktor}
\label{auto_Datenbankname}
\end{table}
\begin{table}[H]
\centering
\begin{tabular}{ c c c c c c}
Gain 0 & Gain 1 & Gain 2 & Gain 3 &  AutoGain & UsedGain \\
\hline
A*0 & A*1 & A*2 & A*3 & A & gainA  \\
B*0 & B*1 & B*2 & B*3 & B & gainB  \\
C*0 & C*1 & C*2 & C*3 & C & gainC  \\
D*0 & D*1 & D*2 & D*3 & D & gainD  \\
E*0 & E*1 & E*2 & E*3 & E & gainE  \\
F*0 & F*1 & F*2 & F*3 & F & gainF  \\
G*0 & G*1 & G*2 & G*3 & G & gainG  \\
H*0 & H*1 & H*2 & H*3 & H & gainH  \\
R*0 & R*1 & R*2 & R*3 & R & gainR  \\
I*0 & I*1 & I*2 & I*3 & I & gainI  \\
S*0 & S*1 & S*2 & S*3 & S & gainS  \\
J*0 & J*1 & J*2 & J*3 & J & gainJ  \\
T*0 & T*1 & T*2 & T*3 & T & gainT  \\
U*0 & U*1 & U*2 & U*3 & U & gainU  \\
V*0 & V*1 & V*2 & V*3 & V & gainV  \\
K*0 & K*1 & K*2 & K*3 & K & gainK  \\
W*0 & W*1 & W*2 & W*3 & W & gainW  \\
L*0 & L*1 & L*2 & L*3 & L & gainL  \\

\end{tabular}
\caption{AS7265X Datenbank-ID bei automatischem Verstärkungsfaktor}
\label{auto_Datenbankname_AS7265X}
\end{table}

\noindent Das Flussdiagramm in Abbildung \ref{fig:autoGainMeasurement} beschreibt den Ablauf für autoGainMeasurementAS7261.
Der Ablauf von autoGainMeasurementAS7265X ist bis auf den SENSORTYP und die Namen der Channel identisch.
\begin{figure}[H]
  \centering
    \caption{Flowchart autoGainMeasurementAS7261}
 
  \label{fig:autoGainMeasurement}
\end{figure}

\subsubsection{matchValueToMaxGain}\label{matchValueToMaxGain}
Die Funktion matchValueToMaxGain passt einen übergebenen Messwert mit dem verwendeten Verstärkungsfaktor von 1x, 3,7x, 16x, 64x, an die maximale Verstärkung von 64x an:
\begin{itemize}
	\item Gain$ 1x \cdot 64 = 64 $ 
	\item Gain$ 3,7x \cdot 17,2972972973 \thickapprox 64 $ 
	\item Gain$ 16x \cdot 4 = 64 $ 
	\item Gain$ 64x \cdot 1 = 64 $ 
\end{itemize}

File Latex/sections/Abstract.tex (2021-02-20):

The goal of this work is to develop a spectral sensor platform using the AS7261 and AS72651, which can be used modularly for different research purposes, but especially for daylight measurements. Since it is not possible to measure in several directions in the sky at the same time with only one of the AS7261 (or AS72651) sensors without mechanical components, it must be ensured that a large number of sensors can be combined into a sensor array in order to be able to measure with directional resolution.\\
The resulting sensor platform uses a Raspberry Pi 4 as central control unit, which communicates with external sensor boards via I2C.
The sensor boards are designed to be connected in series to allow a variety of measurement configurations.
The database and the web interface for displaying and querying the data runs locally on the Rasperrypi.
The thesis describes the development of all hardware and software components.\bigskip

\noindent Ziel dieser Arbeit ist es, mithilfe des AS7261 und AS72651 eine Spektral-Sensor Plattform zu entwickeln, die modular für unterschiedliche Forschungszwecke, aber vor allem zu Tageslichtmessung, genutzt werden kann. Entscheidend dabei ist, dass das System portabel und kosteneffizient umgesetzt wird, um vielfache und flexible messaufbauten zu ermöglichen. Da es ohne mechanische Komponenten nicht möglich ist, mit nur einem der AS7261 (oder auch AS72651) Sensoren in mehrere Richtungen am Himmel gleichzeitig zu messen, muss es möglich sein, eine Vielzahl der Sensoren zu einem Sensor Array zusammenzuschließen, um so richtungsauflösend messen zu können. \\
Die resultierende Sensorplattform nutzt einen Raspberry Pi 4 als zentrale Steuereinheit, welcher über I2C mit externen Sensnorboards kommuniziert.
Die Sensnoroards sind darauf ausgelegt, in reihe geschaltet zu werden, um so eine Vielzahl von Messkonfigurationen zu ermöglichen. Die Datenbank und das Webinterface zum Darstellen und Abfragen der Daten laufen lokal auf dem Raspberry Pi. In der Arbeit sind die entwickelten Hard- und Softwarekomponenten beschrieben.

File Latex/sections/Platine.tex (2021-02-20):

Für diese Arbeit wurden zwei Platinen mit dem EDA\footnote{Electronic design automation}-Programm Eagle entworfen.
Abbildungen des Schaltplans und der Platinen, sowie deren Eagle-Dateien befinden sich im Anhang.
Mit Hilfe von externen Dienstleistern wurden 30 Sensorboards und drei Stauts \& Adapterplatinen angefertigt.

\subsection{System Topologie}
\begin{figure}[H]
\centering
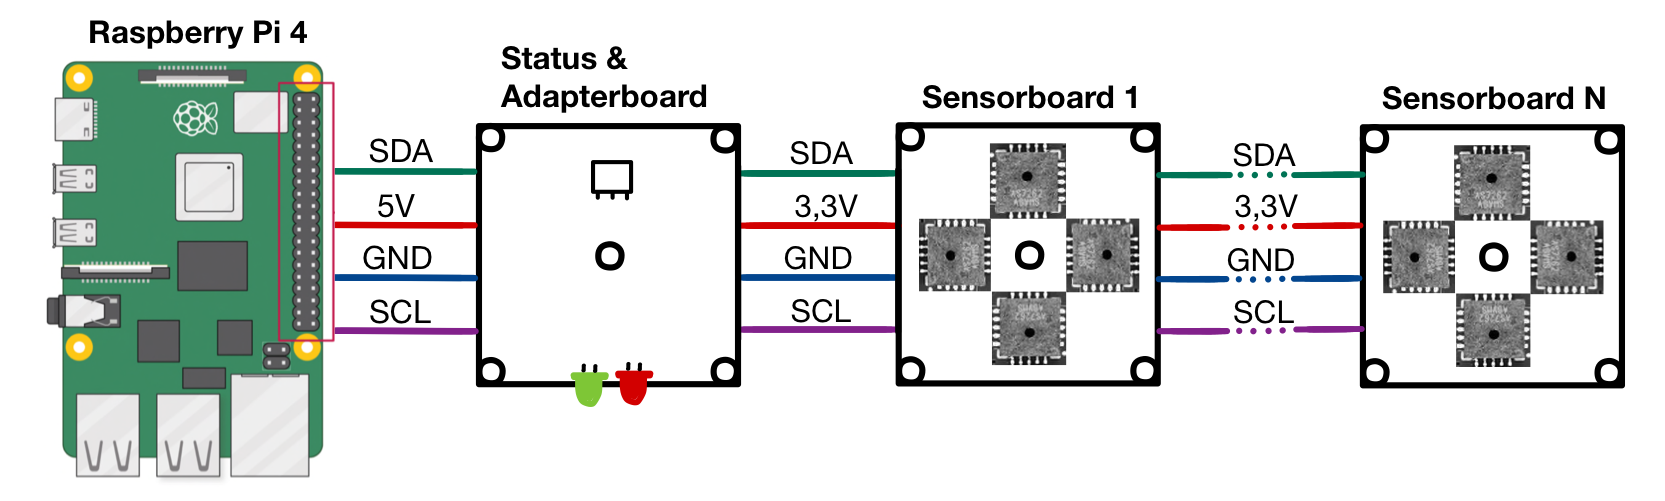
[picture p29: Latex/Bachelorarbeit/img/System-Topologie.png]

\caption{Verschaltung der Platienen \cite{raspberrypi_fundation}}
\label{fig:Verschaltung_der_P}
\end{figure}

Der Messaufbau besteht aus einem Rapberry Pi 4 Model B, welcher über ein Status \& Adapterboard mit 1-10 Sensnorboards verbunden werden kann (Abbildung \ref{fig:Verschaltung_der_P}).

\subsection{Status \& Adapterboard}
Da wie in Abschnitt \ref{Mikrocontroller} erklärt, der Rapberry Pi nicht die benötigte 3,3V Stromversorgung bereitstellt, wird ein Adapterboard (Abbildung \ref{fig:Adapter-Shield}) mit einem Spannungswandler (LM3940IT-3.3) verwendet.
Auf dem Adapterboard findet der einheitliche Steckverbinder sowie die Pullup-Widerstände des I2C Bus Platz. Da das Adapterboard aufgrund seiner Bauform nicht falsch montiert werden kann, kann so die Verpolung der Sensoren ausgeschlossen werden.
Die Bedeutung der Status LED wird im Handbuch unter Abschnitt \ref{leds} erläutert.\\ 
Der überflüssige Platz auf dem Adapterboard wurde für einen Prototyping-Bereich genutzt.

\begin{figure}[H]
\centering

%\caption*{Quelle: Datenblatt AS7261}
\caption{Platine des Status \& Adapterboard}
\label{fig:Adapter-Shield}
\end{figure}
\subsection{Sensorboard}
Die Hauptaufgabe der Sensorboard Platine ist es den AS7261 und der AS7265X mit ihrem Companion Flash (Abschnitt \ref{sec_Companion_Flash}) und über den I2C Translator (Abschnitt \ref{I2C-Translator}) dem I2C Bus zu verbunden.
Außerdem werden verschiedene LEDs, Widerstände und Kondensatoren verbaut, die benötigt werden.

\paragraph{Status LED:} Am AS7261 und AS7265X befindet sich je­weils eine rote Status-LED. Wenn es ein Problem mit dem Companion Flash gibt, fängt sie an zu blinken. Im Normalbetrieb kann die LED softwareseitig ein- und ausgeschaltet werden.
	Während der Messung sollte sie ausgeschaltet werden, da das rote Licht sonst die Messung verfälscht.

\paragraph{Pull-up-Widerstände:}
R7 und R8 sind die Pullup Widerstände des seperaten I2C Bus welcher die AS7265X Sensoren miteinander verbindet.\\
R12 und R11 sind die Pullup Widerstände des I2C Bus welcher den AS7261 mit seinem LCT4316 verbindet.\\
R4 und R5 sind die Pullup Widerstände des I2C Bus welcher den AS72651 mit seinem LCT4316 verbindet.

\paragraph{I2C Enable Widerstände:} Pin R6 ist mit 3.3V und Pin 8 (I2C Enable) des AS7261 verbunden. So wird 
I2C als Kommunikationsmodus des AS7261 ausgewählt.
	R3 erfüllt die gleiche Aufgabe für den AS72651.
	
\paragraph{Translation Byte Widerstände:}
Die 8 Widerstände auf der Rückseite, R1\_XX und R2\_XX, sind die in \ref{I2C-Translator} beschriebenen Widerstände, welche das Translation Byte einstellen. Die Widerstände R1\_XX bestimmen die Addresse des AS7261 und R2\_XX die Addresse des AS72651.

\paragraph{Entstörkondensatoren:} Im Datenblatt der Sensoren wird empfohlen, für jeden Sensor zwei parallele Entstörkondensatoren, mit den Kapazitäten $10uF$ und $100nF$, so nah wie möglich am Sensor zwischen GND und VCC zu platzieren. In Tabelle \ref{kondi} sind die verwendeten Kondensatoren, ihre Abkürzung auf dem Sensorboard und der zugehörige Sensor aufgelistet.

\begin{table}[H]
\centering
\begin{tabular}{ c | c | c }
 Kürzel & Wert & Sensor \\ 
 \hline
 C5 & $10uF$ & AS7261 \\  
 C4 & $100nF$ & AS7261 \\
 C1 & $10uF$ & AS72651 \\  
 C8 & $100nF$ & AS72651 \\
 C2 & $10uF$ & AS72652 \\  
 C3 & $100nF$ & AS72652 \\
 C7 & $10uF$ & AS72653 \\  
 C6 & $100nF$ & AS72653 \\
\end{tabular}
\caption{Entstörkondensatoren}
\label{kondi}
\end{table}

\begin{figure}[H]
\centering

%\caption*{Quelle: Datenblatt AS7261}
\caption{Vorderseite des Sensorboards I2C Leitungsverlauf in rot}
\label{fig:Sensor-platiene_front}
\end{figure}

\begin{figure}[H]
\centering

%\caption*{Quelle: Datenblatt AS7261}
\caption{Rückseite des Sensorboards I2C Leitungsverlauf in rot}
\label{fig:Sensor-platiene_back}
\end{figure}

\paragraph{I2C Lanes:}
Die I2C Leitungen haben ihren Ursprung auf der Adapterplatine und werden mithilfe der seitlichen Steckverbinder über die Sensorboards durchgeschleift.
Die maximal mögliche Länge einer I2C Leitung hängt von der Länge der Leitungskapazität sowie äußeren Störeinflüssen ab.
Die Data und die Clock Leitung sind möglichst weit von anderen Datenleitungen, also auch voneinander entfernt platziert, da so Störeinflüsse durch elektromagnetische Felder minimiert werden.
Außerdem wurde darauf geachtet, dass die beiden Leitungen auf den Platinen die gleiche Länge haben, da sich sonst die Differenzen der Leitungslänge mit jeder angeschlossenen Platine addiert und es zu Timing Differenzen zwischen der Daten und Clock Leitung kommt.
Der Verlauf der Leitungen ist in Abbildung \ref{fig:Sensor-platiene_back} und \ref{fig:Sensor-platiene_front} Rot gekennzeichnet.
\newpage
\noindent \paragraph{Connector:} Es gibt 4 durchkontaktierte Löcher auf der rechten und linken Seite der Platine. Hier können unterschiedliche Steckverbinder mit 2.54 mm Pitch montiert werden.
	Es empfiehlt sich, verpolungssichere Steckverbinder zu verwenden, um Hardware Schäden vorzubeugen.
	Für dieses Bauteil wurde keine SMD-Technik sondern Durchsteckmontage gewählt, da so eine bessere mechanische Festigkeit erreicht wird.
	Außerdem kann so alternativ zu einem Steckverbinder direkt ein Flachbandkabel angelötet werden.

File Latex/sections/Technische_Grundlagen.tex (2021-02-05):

\subsection{Fotodioden}
Photodioden sind beleuchtete pn-Übergänge. Im Kurzschlussbetrieb (U = 0) fließt ein über einen Bereich von mehr als acht Zehnerpotenzen linear von der Beleuchtungsstärke abhängiger Kurzschlussstrom $I_k$ (Abbildung \ref{fig:PhotodiodeKennline})
\cite{Aktive_Bauelemente}.
Dieser setzt sich aus dem durch einstrahlendes Licht verursachten Photostrom und dem temperaturabhängen Dunkelstrom Zusammen \cite{Halbleiterelektronik}.
Allerdings hängt der Photostrom auch von der Absorptionstiefe in das Siliziumsubstrat ab, welche wiederum von der Wellenlänge abhängt (Abbildung  \ref{fig:Silizium-eindingtiefe}) \cite{Solarzellenlicht}

\begin{figure}[H]
  \begin{subfigure}[b]{0.4\textwidth}
  \caption{Kennlinienfeld Photodiode \cite{Aktive_Bauelemente}}
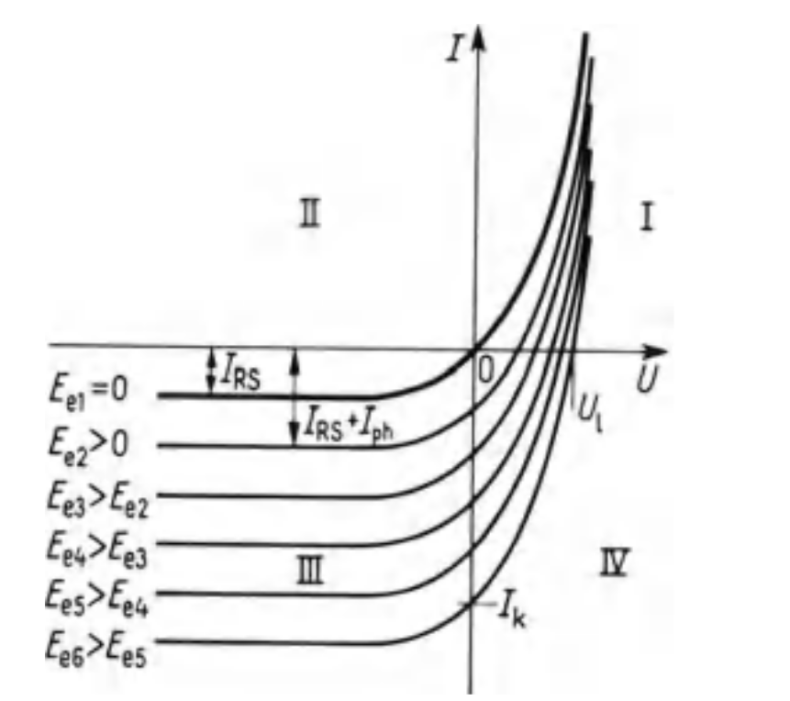
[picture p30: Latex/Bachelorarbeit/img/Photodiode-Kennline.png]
    
    \caption*{Kennlinienfeld $I=f(U)$ der \\Photodiode mit der Bestrah-\\lungsstärke $E_e$ als Parameter\\Kurzschlussstrom $I_k$ bei $U=0$}
    \label{fig:PhotodiodeKennline}
  \end{subfigure}
  %
  \begin{subfigure}[b]{0.55\textwidth}
    \caption{Silizium-Eindringtiefe-Licht \cite{laser}}
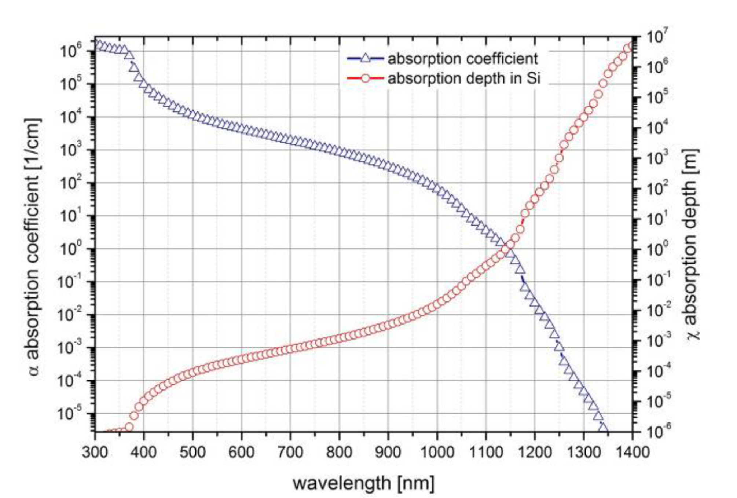
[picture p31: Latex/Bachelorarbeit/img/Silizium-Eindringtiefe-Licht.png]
    
    \caption*{ Optische Eigenschaften von Silizium: Absorptionskoeffizient (Dreiecke) und Absorptionstiefe (Kreise) in Abhängigkeit von der Wellenlänge.}
  \label{fig:Silizium-eindingtiefe}
  \end{subfigure}
\end{figure}

\noindent Damit Rückschlüsse über den Kurzschlussstrom $I_K$ zur Lichtintensität zulässig sind, muss also die Temperatur konstant oder zumindest bekannt sein, da so ein möglichst akkurater temperatur- und frequenzabhängiger Kompensationsfaktor gewählt werden kann.

\newpage
\subsection{I2C}
I2C Alternativ I$^2$C geschrieben, ist ein simples und effizientes Busprotokoll.
Es wurde ursprünglich von Phillips entwickelt, wird aber seit einigen Jahren von NPX weiterentwickelt.
In seiner simpelsten Form ermöglicht es einen Master mit bis zu 128 Slave-Geräten zu verbinden.
Dafür werden nur 2 Leitungen benötigt, die SCL und SDA genannt werden. SCL ist die Taktleitung. Sie wird verwendet, um alle Datenübertragungen über den I2C-Bus zu synchronisieren. SDA ist die Datenleitung.
Alle Busteilnehmer müssen mit dem gleichen GND potential verbunden sein um Stromfluss über die SDA und SCL Leitungen zu ermöglichen\cite{i2b-bus_org}.\\
SCL und SDA benötigen jeweils einen Pull-Up-Widerstand da sie als ”Open Drain” betrieben werden, was bedeutet, dass die Leitungen über Widerstände (Pull-Up-Widerstände) mit der Versorgungsspannung verbunden sind und somit in den High-Zustand gezogen werden.
Die angeschlossenen Geräte ändern den Zustand der Datenleitung auf Low, indem sie die Leitung über einen MOSFET mit GND verbinden.
Um die Leitung wieder auf High zu heben, wird die Verbindung zu GND wieder getrennt und der Pull-Up-Widerstand sorgt dafür, dass die Leitung wieder im High-Zustand ist.\\
Die Clockleitung SCL wird vom Bus Master gesteuert, so kann der Master den Takt der Datenübertragung bestimmen.
Die SDA Leitung wird vom Master und Slave genutzt um Daten zu übertragen. Allerdings antworten die Slaves im Normalbetrieb nur, nachdem sie vom Master auf iher Adresse eine Anfrage erhalten haben. 
Die Spezifikation des Protokolls\cite{nxp_com} empfiehlt die SDA und SCL Leitung möglichst weit voneinander zu entfernen um so Signalstörungen vorzubeugen.

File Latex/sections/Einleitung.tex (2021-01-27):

Es gibt viele wissenschaftliche und industrielle Anwendungen, die zuverlässige Daten über die spektrale Zusammensetzung des menschlich sichtbaren Tageslichts erfordern.\\
Das menschlich sichtbare Licht besteht aus den Wellenlängen der elektromagnetischen Strahlung ($380 - 780 nm$), die ursprünglich von unserer Sonne emittiert werden und direkt oder indirekt die Erde erreichen.
Um das Licht über den gesamten sichtbaren Bereich des Himmels zu erfassen, sind mehrere Sensoren zur Messung in verschiedenen Richtungen oder mechanische Komponenten zur Abtastung des Himmels in mehreren Punkten erforderlich.\\
Das Fachgebiet Lichttechnik benutzt bereits einen Messaufbau. Dieser verwendet einen Spektrometer, der durch einen beweglichen Spiegel und eine rotierbare Basis in der Lage ist, den Himmel abzutasten. 
Der Messaufbau kann somit mit einer sehr genauen spektralen Auflösung von 1 nm in 145 Himmelsbereichen messen.\\
Im Dauereinsatz haben sich mechanische Komponenten unter dem Einfluss äußerer Bedingungen als gravierender Schwachpunkt erwiesen.\\
 Die Messeinrichtung ist aufgund des hochwertigen Sensors in der Lage, sehr genaue Messungen aufzuzeichnen. Die Anschaffung ist jedoch mit erheblichen Kosten verbunden.\\
Aus diesem Grund wird am Fachgebiet für Lichttechnik der Technischen Universität Berlin an einer transportablen, spectral- und richtungsauflösenden Messeinrichtung geforscht, die ohne mechanische Komponeten auskommt und durch die Verwendung von weniger genauen Sensoren eine kostengünstige und robuste Alternative darstellt.

\noindent In dieser Arbeit wird mithilfe der von AMS entwickelten auf Fotodioden basierenden Lichtsensoren  AS7261 und AS7265X eine Spektral-Sensor Plattform entwickelt. Die modular für unterschiedliche Forschungszwecke, aber vor allem zur Tageslichtmessung, genutzt werden kann.

\subsection{Aufbau des Messystems}
Ein Einplatinencomputer wird mit bis zu zwölf AS7261 und zwölf AS7265X Sensoren verbunden.
Die Messungen werden über eine I2C Bus Verbindung gesteuert und ausgelesen.
Auf dem Einplatinencomputer  wird eine Datenbank mit den Messdaten gefüllt und über ein Webinterface, welches auch auf dem Einplatinencomputer gehostet wird, verfügbar gemacht.

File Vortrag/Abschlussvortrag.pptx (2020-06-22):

## Entwicklung und Realisierung einer Messeinrichtung mit den Sensoren AS7261 und AS72651 von ams

Lennard Bödiger | Fachgebiet Lichttechnik | Antrittsvortrag Bachelorarbeit

## Gliederung

Lennard Bödiger | Antrittsvortrag Bachelorarbeit

    1. Hintergrund
    2. Tageslichtmessstation
    3. Umsetzung des Messsystems
    4. Zeitplan
    5. Zusammenfassung

## 1.1 Motivation

Skyscanner auf dem Dach der TU Berlin

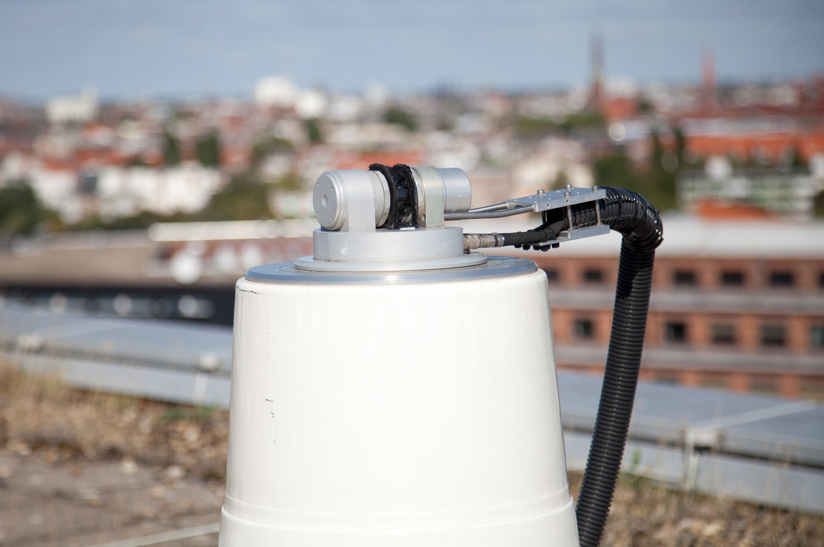
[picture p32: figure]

- 145 Himmelsbereiche
- 336nm bis 970nm [1nm Schritte]
- Umfangreiche Messdaten

- Hoher Anschaffungspreis
- Umfassende Kalibrierungen
- Ortsfest

Abbildung 1: Skyscanner
(Bild: Aicha Diakite, Nils Weber)

## 1.1 Motivation

Kostengünstiger
Spektral- (und Richtungsauflösend?)
Transportabel


Abbildung 2: TrueColour Chip
(Quelle:
https://www.mouser.de/new/ams/ams-as7265x-sensors/)

## 2. Sensoren



## 2. Anforderungsliste ?

## 3. Umsetzung des Messsystems

Adapter &
Satatus
Platine

NanoPi Neo2
Black


SDA

SDA

Sensor
Platine

SDA

Sensor
Platine

GND

SCL

GND

SCL

GND

SCL

5V

3.3V

3.3V

## 3. Umsetzung des Messsystems

Einfach zu Updaten
Dynamisches Grafana Dashboard


## 4. Zeitplan

Arbeitsschritte | Monat
Platine | Juli
Software | August
Testbetrieb | September
Dokumentation & Abschlusspräsentation | September

## 5. Zusammenfassung

- Messsystem zur Ermittlung der direkten Beleuchtungsstärke durch die Sonne auf eine Normalfläche
- Erfassung von Messdaten
- Ermöglicht Berechnungen zur Tageslichtversorgung im Innenraum
- Aufgaben:
    - Wetterfestes Gehäuse
    - Messsignalaufbereitung
    - Temperaturregelung
    - Kalibrierung und Testmessreihe

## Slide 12

Vielen Dank für Ihre Aufmerksamkeit!

## Quellen

- [1] http://www.tecnolight.de/pages/german/news/press/m_schmidt/bild1.jpg
- (29.10.2014)
- [2] „Inbetriebnahme und Optimierung einer Tageslichtmessstation“, Stefan Gramm
- (2006, Studienarbeit)
- [3] http://www.powerfromthesun.net/Book/chapter02/chapter02.html
- (29.10.2014)

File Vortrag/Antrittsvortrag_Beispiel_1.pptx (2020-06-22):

## Entwicklung und Realisierung eines Messsystems zur Bestimmung des Farbspektrums mit variabler Anzahl der Messeinheiten

Lennard Bödiger | Fachgebiet Lichttechnik | Antrittsvortrag Bachelorarbeit

## Gliederung

Lennard Bödiger | Antrittsvortrag Bachelorarbeit

    1. Hintergrund
    2. Tageslichtmessstation
    3. Umsetzung des Messsystems
    4. Zeitplan
    5. Zusammenfassung

## 1.1 Motivation

Skyscanner auf dem Dach der TU Berlin


- 145 Himmelsbereiche
- 336nm bis 970nm [1nm Schritte]
- Umfangreiche Messdaten

- Hoher Anschaffungspreis
- Umfassende Kalibrierungen
- Ortsfest

Abbildung 1: Skyscanner
(Bild: Aicha Diakite, Nils Weber)

## 1.1 Motivation

Kostengünstiger
Spektral- (und Richtungsauflösend?)
Transportabel


Abbildung 2: TrueColour Chip
(Quelle:
https://www.mouser.de/new/ams/ams-as7265x-sensors/)

## 2. Sensoren



## 2. Anforderungsliste ?

## 3. Umsetzung des Messsystems

Adapter &
Satatus
Platine

NanoPi Neo2
Black


SDA

SDA

Sensor
Platine

SDA

Sensor
Platine

GND

SCL

GND

SCL

GND

SCL

5V

3.3V

3.3V

## 3. Umsetzung des Messsystems

Einfach zu Updaten
Dynamisches Grafana Dashboard


## 3. Mögliche Probleme

Intigität der Uhrzeit ohne Internet?

## 4. Zeitplan

Arbeitsschritte | Monat
Platine | Juli
Software | August
Testbetrieb | September
Dokumentation & Abschlusspräsentation | September

## 5. Zusammenfassung

- Messsystem zur Ermittlung der direkten Beleuchtungsstärke durch die Sonne auf eine Normalfläche
- Erfassung von Messdaten
- Ermöglicht Berechnungen zur Tageslichtversorgung im Innenraum
- Aufgaben:
    - Wetterfestes Gehäuse
    - Messsignalaufbereitung
    - Temperaturregelung
    - Kalibrierung und Testmessreihe

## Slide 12

Vielen Dank für Ihre Aufmerksamkeit!

## Quellen

- [1] http://www.tecnolight.de/pages/german/news/press/m_schmidt/bild1.jpg
- (29.10.2014)
- [2] „Inbetriebnahme und Optimierung einer Tageslichtmessstation“, Stefan Gramm
- (2006, Studienarbeit)
- [3] http://www.powerfromthesun.net/Book/chapter02/chapter02.html
- (29.10.2014)

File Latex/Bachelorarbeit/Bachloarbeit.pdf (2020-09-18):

Technische Universit¨at Berlin
Fakul¨at IV
Institut fu¨r Energie- und Automatisierungstechnik Fachgebiet Lichttechnik

# Entwicklung und Realisierung einer Messeinrichtung mit den Sensoren AS7261 und AS72651 von ams

### Bachlorarbeit

## Vorgelegt von: Lennard B¨odiger Matrikelnr.: 363470 Studiengang: Technische Informatik

## 18. September 2020

## 1 Einleitung

## 2 Technische Grundlagen

### 2.1 Fotodioden

Photodioden sind beleuchtete pn-U¨berg¨ange. Im Kurzschlussbetrieb (U = 0) fließt ein u¨ber einen Bereich von mehr als acht Zehnerpotenzen linear von der Beleuchtungsst¨arke abh¨angiger Kurzschlussstrom Ik (Abb. 1a). Allerdings h¨angt der Kurzschlussstrom auch von der Eindringtiefe in das Silizium Substrat ab, welche wiederum von der Wellenl¨ange abh¨angt (Abb 1b). Außerdem ¨andert sich der sich der Absorptionskoeffizient von Silizium mit der Temperatur.

Ich habe die Sensoren mit Luft gel¨otet, aber da dieses QFN Package einfach ein Pain zum L¨oten ist, brauche ich immer mal wider mehrere versuche, und fru¨her oder sp¨ater l¨auft mir Flussmittel in den Sensor/ ich brenne ihn an weil ich zu lange auf einer Stelle bleibe. Das sind also alles Probleme, die mit etwas Kapton Tape auf der Sensor O¨ffnung und mehr U¨bung zu l¨osen sind, aber es w¨are super mal ein sauberes referenboard zu haben.

(a) Kennlinienfeld Photodiode

Kennlinienfeld I = f(U) der Photodiode mit der Bestrah- lungsst¨arke Ee als Parameter; (b) Silizium-Eindringtiefe-Licht

Kurzschlussstrom Ik bei U = 0

Quelle: osioptoelectronics.com

Damit Ru¨ckschlu¨sse u¨ber den Kurzschlussstrom IK zur Lichtintensit¨at zul¨assig sind, muss also die Temperatur konstant oder zumindest bekannt sein. Außerdem ist es wichtig, bei Tageslichtmessungen, dass einfallende Licht auf eine m¨oglichst begrenzten Wellenl¨angenbereich zu beschr¨anken, da so ein m¨oglichst akkurater Temperatur und Frequenzabh¨aniger kompensations faktor gew¨ahlt werden kann.

2.2 I2C

I2C ist ein siples und effizentes Busprotokoll. Es wurde urspru¨nglich von phillips entwikelt, wird aber seit einigen jahren von NPX weiterentwikelt. In seiner simpelsten form erm¨oglicht es einen Master mit bis zu 128 Slave ger¨aten zu verbinden. Dafu¨r werden nur 2 leitungen ben¨otigt, die die SCL und SDA genannt werden. SCL ist die Taktleitung. Sie wird verwendet, um alle Datenu¨bertragungen u¨ber den I2C-Bus zu synchronisieren. SDA ist die Datenleitung. Außerdem mu¨ssen alle Bus teilnehmer mit dem gleichen GND potential verbunden sein um stromfluss u¨ber SDA und SCL leitungen zu erm¨oglichen.

Da SCL und SDA als “open drain” betrieben werden, was bedeutet das die Bus teilnehmer den output low aber nicht high setzen k¨onnen, muss ein Pull up Wiederstand zur versorgungspannung verwendet werden.

Die Clock leitung SCL wird nur vom Bus Master gesteuert. Die SDA leitung wird vom Master und Slave genutzt allerdings antworten die Slaves im normalbetrieb nur nachdem sie vom master auf iherer Adresse eine einfage erhalten haben. Die Spezifikation des Protokolls empfiehlt die SDA und SCL Leitung m¨oglichst weit voneinander zu entfernen um so die Signalqualit¨at zu verbessern.

## 3 Hardware Komponenten

### 3.1 Sensoren

Abbildung 2: AS726X

Die Sensoren aus der AS726X Reihe sind in der lage Licht, also elektromagnetische Strahlung zu messen. In jedem Sensor sind 6 Photodioden verbaut. Vor jeder Photodiode ist ein Silizium-Interferenzfilter montiert, welcher wie ein Bandpassfilter arbeitet, er ist nur fu¨r einen bestimmten Ausschnitt des Lichtspektrums durchl¨assig. Jeder Baustein enth¨alt einen Analog-digital-Wandler mit 16 Bit Aufl¨osung, der den Strom aus den unterschiedlichen Fotodioden integriert. Nach Abschluss einer Messung wird das integrierte Ergebnis in die entsprechenden Datenregister u¨bertragen.


So kann u¨ber das beschriebene Sensorarray die farbliche Zusammensetzung des eingestrahlten Lichts erfasst werden.

Abbildung 3: Seitenasicht AS726X


Quelle: Datenblatt AS7261

Wie in Abb:18 dargestellt, f¨allt das Licht durch die O¨ffnung in der Mitte des Sensors ein, eine intern verbaute Linse verteilt das Lich auf die Interferenzfilter. Die Genauigkeit der Filter ver¨andert sich je nach Einstrahlwinkel, daher ist es wichtig, vor den Sensor noch eine Streuscheibe zu montieren.
Gemessenen Daten k¨onnen u¨ber UART oder I2C an einen Mikrocontroller u¨bertragen werden, da u¨ber UART nur ein Ger¨at verbunden werden kann, eignet sich aber fu¨r diesen Anwendungsfall nur die I2C Schnittstelle.
Alle Sensoren erhalten vom Hersteller dieselbe nicht ver¨anderbare I2C Adresse: 0x49. Daher muss ein I2C Translator genutzt werden, welcher es erm¨oglicht, mehrere Sensoren im gleichen Bussystem zu adressieren(siehe Abschnitt 3.3).

Die Modelle unterscheiden sich durch die verbauten Silizium-Interferenzfilter, also die unterscheidbaren Wellenl¨angenbereiche sowie in der ben¨otigten Peripherie. Die grunds¨atzliche Messmethode ist aber immer gleich. Im Folgenden werden die verwendeten Sensoren AS7261(3.1.1) sowie der AS7265X(3.1.2) beschrieben.

3.1.1 AS7261

Das Sensorarray des AS7261 unterscheidet zwischen X,Y,Z,C,D und NIR.

Abbildung 4: AS7261-Sensor Array


Quelle: Datenblatt AS7261

Die Ergebnisse des ADC werden direkt, ohne das der Temperaturdrift der Photodioden beru¨cksichtigt wird in die in Tabelle 1 beschrieben Register geschrieben.

Tabelle 1: Your caption.
ku¨rzel | Bezeichnung | Register | Filtereigenschaften
C | Clear | 0x12-0x13 | kein Filter
D | Dark | 0x10-0x11 Lichtdurchl¨assigkeit des Geh¨auses
NIR | nahes Infrarot 0x0E-0x0F | ?????
X | X (CIE 1931) | 0x08-0x09 | ????
Y | X (CIE 1931) 0x0A-0x0B | ????
Z | X (CIE 1931) 0x0C-0x0D | ?????

Da die Messergebnisse der unterschiedlichen Wellenl¨angenbereiche den in ?? genannten Verzerrungen unterliegen, werden auch noch berichtigte X,Y,Z-Werte bereitgestellt.

ku¨rzel | Register | Berichtigungs Formel
Cal-X | 0x14:0x17 | ????
Cal-Y | 0x18:0x1B | ????
Cal-Z 00x1C:0x1F | ?????

Abbildung 5: AS7261-Bank Modes

Es gibt 3 sogenannte Bank Modes in denen der Sensor Arbeiten Kann. Bank Mode 0
Die Konvertierungen erfolgen kontinuierlich und Daten sind in den I2C-Registern X, Y, Z und NIR verfu¨gbar.
Bank Mode 1
Die Konvertierungen erfolgen kontinuierlich und Daten sind in den I2C-Registern X, Y, D und C
verfu¨gbar.
Bank Mode 2


Die Konvertierungen erfolgen kontinuierlich, und Daten sind nach zwei Integrationsperioden in den Registern X, Y, Z, NIR, D und C verfu¨gbar. In diesem Modus k¨onnen dauch die kalibrierten, korrigierten Werte auch aus den entsprechenden I2C-Registern abgerufen werden. Bank Mode 3
Die Konvertierungen erfolgen nur einmal, und Daten sind wie in Bank Mode 2 nach zwei Integrationsperioden in den Registern X, Y, Z, NIR, D und C verfu¨gbar. Auch Die kalibrierten, korrigierten Werte auch aus den entsprechenden I2C-Registern k¨onnen abgerufen werden. Das DATA RDY-Bit wird auf 1 gesetzt, sobald Daten verfu¨gbar sind.
Fu¨r diesen Anwendungsfall wird Bankmode 3 verwendet da so an alle angeschlossenen sensoren m¨oglichst gleichzeitig eine messung gestartet werden kann. Die daten k¨onnen nach abgeschlossener messung an den NanoPi u¨bertragen werden.


Abbildung 6: AS7261-Sensor Array

3.1.2 AS7265X

AS7265X beschreibt AS72651, AS72652 und AS72653 wobei der AS72651 als master fu¨r AS72652 und AS72653 fungiert indem er u¨ber einen weiteren separaten I2C Bus ihre Daten abfragt und ansonsten wie der AS7261 arbeitet.


Abbildung 7: S7265X-Scematic


Abbildung 8: AS7261-Spectral Responsivity

Die drei Sensoren messen in Kombination mit 18 unterschiedliche Photodioden, so k¨onnen 18 unterschiedliche Frequenz Channel im Bereich zwischen 410 nm und 940 nm mit einer Halbwertsbreite von jeweils 20 nm erfassen. Die Frequenz Channel sind wie in Abb: TODO zu sehen mit den Buchstaben A-L gekennzeichnet.

### 3.2 Mikrocontroller

Bei der Auswahl des Mikrocontrollers ist die kleine Bauform, ausreichend langlebiger Speicher sowie eine Netzwerkschnittstelle und I2C Anschluss entscheidend.
Die abfrage der Messdaten, sowie die Messkonfiguration soll u¨ber einen Fernzugriff m¨oglich sein. Die Daten sollen grafisch in einem Webinterface dargestellt werden ohne das eine weitere Server Instanz ben¨otigt wird. Daher eignet sich ein Linux f¨ahiger Einplatinencomputer besser als ein simplerer Mikrocontroller. Außerdem erm¨oglicht ein Einplatinencomputer einfache nachtr¨agliche A¨nderungen ohne das eine komplexe Entwicklungsumgebung eingerichtet werden muss.

Der NanoPi NEO2 Black erfu¨llt alle diese Anforderungen:

Abmessungen | 4 cm x 4 cm
Speicher | eMMC Flash Module Socket
Anschlu¨sse | 10/100/1000M Ethernet
GPIO | UART, I2C, IO
RAM | 1 GB
CPU | Allwinner H5 Quad-Core Cortex-A53
Preis | TODO


Abbildung 9: NanoPi NEO2 Black

An den eMMc Socket kann bis zu 128 GB Flash speicher angeschlossen werden. TODO warum reichen 32 GB.
Da eine kabelgebundene L¨osung mehr Zuverl¨assigkeit bietet, wird eine Netzwerkverbindung u¨ber Ethernet einer WLAN-Schnittstelle vorgezogen. Es besteht aber die M¨oglichkeit, einen externen USB WLAN-Adapter nachzuru¨sten.
Die I2C Schnittstelle des NanoPi arbeitet mit 3.3V allerdings wird nur ein 5V und kein 3,3V Output bereitgestellt, daher muss ein steppdown Wandler verwendet werden, um die Sensorboards mit Strom zu versorgen.
Die CPU ist fu¨r den Anwendungsfall weitaus ausreichend dimensioniert. In Abbildung 10 ist ein Performancetest zu sehen, die reihen 1-4 beschreiben die prozentuale CPU Auslastung der jeweiligen Prozessorkerne. Mem beschreibt die Auslastung des Arbeitsspeichers.
Fu¨r den Performancetest wurde eine Messung an 10 Sensor Boards mit minimalem Messintervall gestartet. Außerdem wurden gleichzeitig Daten u¨ber Grafana exportiert.
TODO: Richtiges Bild Performance Test

Abbildung 10: CPU-Performance


### 3.3 I2C Address Translator LTC4316

Da, wie in Abschnitt 3.1 genannt alle Sensoren unter derselben I2C Addresse erreichbar sind, wird ein I2C Translator genutzt, um fu¨r eine individuelle Adressierung zu sorgen.


Abbildung 11: I2C-Bus im Messaufbau

Wie in Abb 11 zu sehen wird fu¨r jeden Sensor ein LTC4316 an die Busschnittstelle des Nano-Pi angeschlossen.(SDAIN, SCLIN).

An jeden LTC4316 wird ein AS7261 oder AS72651 angeschlossen.(SDAOUT, SCLOUT) Bei Kommunikation vom Nano-Pi zum Sensor wird dann die I2C Adresse mit einem Faktor (Translation Byte) welcher mit diskreten Widerst¨anden eingestellt wird mit Fomel 1 verrechnet, um so die Adresse anzupassen.(XORH,XORL). Um das Translation Byte einzustellen mu¨ssen die Widerst¨ande bla,bla und bla wie in Abb ?? am LTC4316 angeschlossen werden.

SensorAdresse ⊕ TranslationByte = NeueAdresse | (1)

Abbildung 12: Translation
Byte

Beispiel Rechnung
0x49 ⊕ 0x01 = 0x48
0x49 ⊕ 0x02 = 0x4b
0x49 ⊕ 0x05 = 0x4c
0x49 ⊕ 0x06 = 0x4f
0x49 ⊕ 0x0A = 0x43
0x49 ⊕ 0x49 = 0x00


In Tabelle 2 und 3 sind die unterschiedlichen Konfigurationen des Translation Bytes aufgelistet.
Im Handbuch ?? ist eine Liste zu finde welche Translation Bytes bereits verwendet werden. Wenn weitere Sensor Boards angefertigt werden ist die Liste dort weiter zu pflegen.

Tabelle 2: Untere 4 Bit des Translation Byte
a3 | a2 | a1 | a0 | RLT | RLB
0 | 0 | 0 | 0 | Open | Short
0 | 0 | 0 | 1 | 976 | 102
0 | 0 | 1 | 0 | 976 | 182
0 | 0 | 1 | 1 | 1000 | 280
0 | 1 | 0 | 0 | 1000 | 392
0 | 1 | 0 | 1 | 1000 | 523
0 | 1 | 1 | 0 | 1000 | 681
0 | 1 | 1 | 1 | 1000 | 887
1 | 0 | 0 | 0 | 887 | 1000
1 | 0 | 0 | 1 | 681 | 1000
1 | 0 | 1 | 0 | 523 | 1000
1 | 0 | 1 | 1 | 392 | 1000
1 | 1 | 0 | 0 | 280 | 1000
1 | 1 | 0 | 1 | 182 | 976
1 | 1 | 1 | 0 | 102 | 976
1 | 1 | 1 | 1 | Short | Open

Tabelle 3: Obere 3 Bit des Translation Byte
a6 | a5 | a4 | RLT | RLB
0 | 0 | 0 | Open | Short
0 | 0 | 1 | 976 | 102
0 | 1 | 0 | 976 | 182
0 | 1 | 1 | 1000 | 280
1 | 0 | 0 | 1000 | 392
1 | 0 | 1 | 1000 | 523
1 | 1 | 0 | 1000 | 681
1 | 1 | 1 | 1000 | 887

### 3.4 Companion Flash

Die Sensoren AS7261 und AS72651 ben¨otigen einen flash speicher von welchem sie ihre Firmware laden k¨onnen. Die jeweilige Firmware von AMS wird mithilfe von Flashcat-USB, einem

USB Memory Programmer u¨ber das SPI Protokoll auf den den Flash Speicher u¨bertragen. Der AT25SF041-SSHD-B wurde aus der von AMS bereitgestellten liste kompatiebler Flash speichern ausgew¨ahlt da er am gu¨nstigsten ist. Da die Firmware nur auf nachfrage bei AMS erh¨altlich. Fu¨r den Messaufbau werder folgende versionen verwendet die .bin files sind im anhang zu finden.
AS7261 complete ??
AS726X AS7265 complete moonlight v1 ??

## 4 Platine

4.0.1 System Topologie


Abbildung 13: Verschaltung der der Platienen

Der Msssaufbau besteht aus einem NanoPi Neo2 Black welcher u¨ber eine status und Adapterplatinene mit 1-10 Sensnorboards verbunden werden kann.

4.0.2 Status & Adapterboard

Da der NanoPi nicht die ben¨otigte 3, 3V Stromversorgung bereitstellt wird eine Adapter-Shield mit einem Spannungswandler(LM3940IT-3.3) verwendet. Sollte der vom NanoPi bereitgestellte Strom nicht ausreichen kann eine externe Stromversorgung an connector j3 auf der adapterplatine angeschlossen werden. Auf dem Adapter-Shield findet der einheitliche Steckverbinder Platz, da das Adapter-Shield aufgrund seiner Bauform nicht falsch montiert werden kann so die Verpolung der Sensoren ausgeschlossen werden. Die Bedeutung der Status LED wird im Handbuch ?? erl¨autert.


Abbildung 14: Verschaltung der der Platienen

4.0.3 Sensorboard

Die hauptaufgabe der Sensorboard Platine ist es den AS7261 und der AS7265X mit ihrem companion flash (??) und u¨ber den I2C Translator (??) dem I2C Bus verbunden. Außerdem werden verschiednene LED, Wiederst¨ande und Kondensatoren verbaut.


Abbildung 15: Verschaltung der der Platienen


Abbildung 16: Verschaltung der der Platienen

Status LED: Am AS7261 und AS7265X Befindet sich jemals eine Rote Status LED wenn es ein problem mit dem Compainin Flash gibt f¨angt sie an zu blinken im normalbetrieb kann die LED Softwareseitg ein und ausgeschaltet werden. W¨arend der Messubng solle sie ausgeschaltet werden da das Rote licht sonst die messung verf¨alscht.

Pull-up-Widerst¨ande: R7 und R8 sind die Pullup Widerst¨ande des seperaten I2C Bus welcher die AS7265X Sensoren miteinander verbindet.
R12 und R11 sind die Pullup Widerst¨ande des I2C Bus welcher den AS7261 mit seinem LCT4316 verbindet.
R4 und R5 sind die Pullup Widerst¨ande des I2C Bus welcher den AS72651 mit seinem LCT4316 verbindet.

I2C Enable Wiederst¨ande: Pin R6 ist mit 3.3V und Pin 8 (I2C Enable) des AS7261 verbunden. So wird der AS7261 in den I2C modus gebracht. R3 erfu¨llt die gleiche Aufgabe fu¨r den AS72651.

Translation Byte Wiederst¨ande: Die 8 Wiederst¨ande auf der Ru¨ckseite R1 XX und R2 XX sind die in ?? beschriebenen wiederst¨ande welche das Translation Byte einstellen. Die wiederst¨ande R1 XX bestimmen die Addresse des AS7261 und R1 XX die Addresse des
AS72651.

Entst¨orkondensatoren: Das Datenblatt der Sensoren emphielt fu¨r jeden Sensor 2 Entst¨orkondensatoren m¨oglichst nah am Sensor zwischen GND und VCC anzubringen.

Ku¨rzel | Wert | Sensor
C5 | 10uF | AS7261
C4 | 100nF | AS7261
C1 | 10uF | AS72651
C8 | 100nF AS72651
C2 | 10uF | AS72652
C3 | 100nF AS72652
C7 | 10uF | AS72653
C6 | 100nF AS72653

I2C Lanes: Die I2C lanes haben ihren ursprung auf der Adapterplatinene und werden mithilfe der seitlichen connectoren u¨ber die Sensnsor boards durschgeschleift. Die maximal m¨ogliche l¨ange einer I2C Leitung h¨angt von der l¨ange der Leitungskapaziet¨at sowie ¨außeren St¨oreinflu¨ssen ab. Die Data und die Clock Leitung sind m¨oglichst weit von anderen Datenleitungen also auch von einander entfernt platziert, da so st¨oreinflu¨sse durch eletromagitisches felder minimiert werden. Außerdem wurde darauf geachtet das die leitungen auf den platinen die gleiche l¨ange habe da sich sonst die differenzen der Leitungs l¨ange mit jeder angeschlossenen Platine addiert und es zu Timing differnezn zwischen der Daten und clock Leitung kommt. Der Verlauf der Leitungen ist in Abb?? Rot gekennzeichnet.

Connector: An den Seiten der platiene befinden sich 4 durchkontaktierte L¨ocher, hier k¨onnen unterschiedliche connectoren mit 2.54 mm pitch montiert werden. Es empfiehlt sich verpolungssichere connectoren zu verwenden, um hardware sch¨aden vorzubeugen. Fu¨r dieses

Bauteil wurde keine SMD-Technik sonder durchkontaktierten Anschlussdr¨ahten gew¨ahlt da so eine bessere mechanische Festigkeit erreicht wird.

Der Connector ist ein 2.54 mm pitch through hole socket. Er wird verwendet da es viele

## 5 Software

### 5.1 wiringPi

Der NanoPi Neo2 Black kommt mit einem vorinstallierten Fork von der wiringPi Libarry https://github.com/friendlyarm/WiringNP/blob/master/wiringPi/wiringPi.c Die funktionalit¨at der drei verwendetetn C-Funktionen werden im folgenden beschrieben.

5.1.1 wiringPiI2CSetup

Der Funktion wird beim audfruf die I2C Adresse u¨bergeben mit welcher eine verbindung aufgebaut werden soll: wiringPiI2CSetup(address).
Der Ru¨ckgabewert ist der Standard Linux File Disciptor oder -1, falls ein Fehler auftritt. Die Anzahl der File Desciptoren ist begrenzt daher muss die verbindung mit der Funktion close() aus der Library: unistd.h geschlossen werden wenn sie nicht mehr ben¨otigt wird.

5.1.2 wiringPiI2CWriteReg8

Der Funktion wird bei aufruf der File Desciptor einer I2C verbindung sowie ein ziel register und die zu schreibenden 8bit Daten u¨bergeben: wiringPiI2CWriteReg8 (fd, RegAdr, 8-Bit-Data). Wenn der Schreibzugriff vom I2C ger¨at best¨atigt wurde wird eine 0 zuru¨ck gegeben.

5.1.3 wiringPiI2CReadReg8

Der Funktion wird bei aufruf der File Desciptor einer I2C verbindung sowie ein ziel register u¨bergeben: wiringPiI2CReadReg8(fd, RegAdr). Der ausgelsene 8-Bit inhalt des Register ist der ru¨chgabewert. Wenn das Lesen Fehlschl¨agt bleibt das Programm in einer Endlosschleife h¨angen.

### 5.2 AS726X Libary

Die WiringPi AS726X Libary enth¨alt alle funktionen um den AS7261 und AS7265X zu steuern und auszulesen. Da die Beispielimplementierungen im Datenblatt in vielen detaifragen ungenau und Fehlerhaft ist wurde die Arduino OpenSource Libarrys von sparkfun Spark-Fun AS726X Arduino Library-master und SparkFun AS7265x Arduino Library als implementierungs grundlage verwendet. Im ersten schritt der entwirklung wurde sie fu¨r die I2C schnittschelle WiringPi des NanoPi umgeschrieben und anschließen in ihrer Funktionalit¨at erweitert um fu¨r das messystem mit mehreren sensoren auf dem gleichen bus nutzbar zu sein.

Im Folgenden Text werden die Register Adressen und mit den gleichen Namen wie im source code bezeichnet die Numerische Adressen sind in Tabelle ?? aufgelistet. TODO table


Abbildung 17: PysicalRegister


Abbildung 18: AS726x CONTROL SETUP

5.2.1 virtualWriteRegister

Wie bei Embeddet ger¨aten u¨blich werden Einstellungen auf dem sensor ver¨andern indem verschiedene sogenannte Special function registers mit daten beschrieben werden.
Jedes Special function register ist 8Bit groß und hat eine adresse und jedes Bit des Register representiert eine einstellung. Beispielsweise ist 0x07 das LED Control Register des Sensors. Bit 0 des Registers Beschreibt den Zustand der Status LED. Die Restlichen 7 Bit des Registers Beschreibt den Zustand anderer LEDs die fu¨r den Messaufbau aber irrelevant sind.
Wird register 7 mit dem Dezimal wert 0 beschrieben sind alle LED aus, wird es mit dem Dezimal wert 1 beschrieben leuchtet ist nur die status LED. Die Register Lassen sich aber nicht direkt Beschreiben, stattdesswen sind sie als sogennate Virtuelle Register Implementiert.

Der Sensor arbeitet mit virtuellenRegistern. Das heißt das nur Register 0x01 (WRITE Register) beschrieben werden kann. Um daten in eins der Special Funktions Register zu schreiben wird die funktion virtualWriteRegister verwendet. Die Funtionsweise l¨asst sich in 4 schritten zusammnefassen:

- Zeile TODO Warten bis das WRITE Register leer ist, was angezeigt wird indem das Bit AS72XX TX VALID im Register AS72XX STATUS REG den wert 1 annimmt.
- Zeile TODO Schreibe die Virtuelle Adresse in das WRITE Register und Setze zus¨atzlich Bit 8 des WRITE Register auf 1 um zu zeigen das es sich um einen Schreibenden zugriff auf das Virtuelle Register handelt.

- Warte erneut bis das WRITE Register leer ist.
- Schreibe die Daten in das WRITE Register

Der Sensor wird jetzt selber die u¨bertragenen Daten aus dem WRITE Register angebene Virtuelle Register kopieren.

1
2 // Write to a virtual register in the AS726x
3 void virtualWriteRegister ( uint8_t virtualAddr , uint8_t ←↪ dataToWrite , int fd){
4 | uint8_t status ;
5 | // Wait for WRITE register to be empty
6 | while (1) {
7 | status = wiringPiI2CReadReg8 (fd , AS72XX_SLAVE_STATUS_REG );
8 | if (( status & AS72XX_SLAVE_TX_VALID ) == 0) {
9 | break ; // No inbound TX pending at slave . Okay to ←↪
write now .
10 | }
11 | delay ( POLLING_DELAY );
12 | }
13 | // Send the virtual register address ( setting bit 7 to ←↪
indicate a | write a register ).
14 | wiringPiI2CWriteReg8 (fd , AS72XX_SLAVE_WRITE_REG , ←↪
( virtualAddr | 0x80));

15
16 | // Wait for WRITE register to be empty
17 | while (1)
18 | {
19 | status = wiringPiI2CReadReg8 (fd , ←↪
AS72XX_SLAVE_STATUS_REG );
20 | if (( status & AS72XX_SLAVE_TX_VALID ) == 0){
21 | break ; // No inbound TX pending at slave . Okay to ←↪
write now .
22 | }
23 | delay ( POLLING_DELAY );
24 | }
25 | // Send the data to complete the operation .
26 | wiringPiI2CWriteReg8 (fd , AS72XX_SLAVE_WRITE_REG , ←↪
dataToWrite );

27 }

5.2.2 virtualReadRegister

Die Unterschiedlichen Messdaten des Sensors werden in dedizierten registern gespeichert. Es ist aber nur u¨ber den indirekten weg des AS72XX READ REG und der Virtuellen Register Adressen m¨oglich daten auszulesen. Die Funktionsweise der zum Daten auslesen ben¨otigten funktion virtualReadRegister l¨asst sich wieder in 4 schritte aufteilen.

- Das AS72XX READ REG wird ausgelesen ohne das die daten verabeitet werden. Dieser schritt ist wie ein Reset des Registers zu verstehen.
- Zeile TODO Schreibe die Virtuelle Adresse in das WRITE Register und Setze zus¨atzlich Bit 8 des WRITE Register auf 0 um zu zeigen das es sich um einen Lesenden zugriff auf das Virtuelle Register handelt.
- Sobald das AS72XX STATUS REG den wert AS72XX TX VALID annimmt sind die Daten aus dem angebenen Virtuellen Register in das AS72XX READ REG kopiert worden.
- Lese die Daten aus dem S72XX READ REG

1 // Read a virtual register from the AS726x
2 uint8_t virtualReadRegister ( uint8_t virtualAddr , int fd){
3 | uint8_t | status ;
4 | // Do a prelim check of the read register
5 | status = | wiringPiI2CReadReg8 (fd , AS72XX_SLAVE_STATUS_REG );
6 | if (( status & AS72XX_SLAVE_RX_VALID ) != 0){ // There is data ←↪
to be read
7 | /* uint8_t incoming = */ wiringPiI2CReadReg8 (fd , ←↪
AS72XX_SLAVE_READ_REG ); // Read the uint8_t but do ←↪ nothing with it
8 | }
9 | // Wait for WRITE flag to clear
10 | while (1) {
11 | status = wiringPiI2CReadReg8 (fd , ←↪
AS72XX_SLAVE_STATUS_REG );
12 | if (( status & AS72XX_SLAVE_TX_VALID ) == 0){
13 | | break ; // If TX bit is clear , it is ok to write
14 | }
15 | delay ( POLLING_DELAY );
16 | }
17 | // Send the virtual register address (bit 7 should be 0 to ←↪
indicate we are reading a register ).
18 | wiringPiI2CWriteReg8 (fd , AS72XX_SLAVE_WRITE_REG , ←↪

virtualAddr );

19
20 | // Wait for READ flag to be set
21 | while (1)
22 | {
23 | status = wiringPiI2CReadReg8 (fd , ←↪
| AS72XX_SLAVE_STATUS_REG );
24 | if (( status & AS72XX_SLAVE_RX_VALID ) != 0) break ; // ←↪
| Read data is ready .
25 | delay ( POLLING_DELAY );
26 | }

27
28 | uint8_t incoming = wiringPiI2CReadReg8 (fd , ←↪
| AS72XX_SLAVE_READ_REG );
29 | return ( incoming );

30 }

5.2.3 MeasurementFromAdress

Die Funktion baut einen I2C Verbindung zur u¨bergebenen Bus-Adresse auf und ruft die Funktion takeMeasurments mit dem File Descriptor der aktiven I2C Verbindung auf. Nachdem die Funktion takeMeasurements durchlaufen ist wird die I2C Verbindung wieder geschlossen.

1 // Calls takeMeasurements on gives I2C Adrress
2 void MeasurementFromAdress ( int address ){
3 | int fd = | wiringPiI2CSetup ( address );
4 | if (fd == -1) {
5 | printf ("i2c failed ");
6 | }
7 | takeMeasurements (fd); | // takesMeasurmant Readings can now ←↪
be accessed via getX () , getY () , etc
8 | close (fd);

9 }

5.2.4 takeMeasurements

Die Funktion takeMeasurements ruft die Funktion setMeasurementMode mit dem Parameter 3 auf das setzt den aus ?? bekannten Bankmode der u¨bergebenen I2C Verbindung (fd) auf Bank Mode 3. Die On-Shot Messung wird sofort gestartet, in Zeile 9 wird gewartet bis die

Messung abgeschlossen ist. Um sicherzustellen das die funktion DataAvailable richtig arbeitet muss vor der Messung das Flag DataAvailable auf 0 gesetzt werden (Zeile 3). Die Daten werden hier nicht ausgelesen daher gibt es keinen ru¨ckgabewert.

1 // Tells IC to take measurements and polls for data ready flag 2 void takeMeasurements (int fd) {
3 | clearDataAvailable (fd); // Clear DATA_RDY flag when using ←↪
| Mode 3

4
5 | // Goto mode 3 for one shot measurement of all channels
6 | setMeasurementMode (3, fd);

7
8 | // Wait for data to be ready
9 | while ( dataAvailable (fd) == 0) delay ( POLLING_DELAY ); ←↪
| // Potential TODO : avoid this to get faster nearly ←↪
| parralel mesurments

10
11 | // Readings can now be accessed via getViolet () , getBlue () , ←↪
| etc

12 }

5.2.5 setMeasurementMode

Mit der Funktion setMeasurementMode werden die Bankmode Bits 2 und 3 des AS726x CONTROL SETUP Registers mit dem gewu¨nschten wert fu¨r den Bankmode beschrieben.
Da die anderen Bits des Registers noch weitere einstellungen repr¨asentieren welche nicht
ver¨andert werden sollen, muss das register erst ausgelsen werden. Anschließend werden die
Bankmode Bits auf 0 gesetzt um im n¨achsten schritt mit dem gewu¨nschten neuen Bankmode wert beschrieben zu werden. Die Bedeutung der Bankmodes ist in ?? erleutert.

1 // Sets the measurement mode
2 // Mode 0: Continuous reading of VBGY (7262) / STUV (7263)
3 // Mode 1: Continuous reading of GYOR (7262) / RTUX (7263)
4 // Mode 2: Continuous reading of all channels (power -on default ) 5 // Mode 3: One - shot reading of all channels
6 void setMeasurementMode ( uint8_t mode , int fd) {
7 | if ( mode > 0b11 ) mode = 0 b11;

8
9 | // Read , mask /set , write

10 | uint8_t value = virtualReadRegister ( AS726x_CONTROL_SETUP , ←↪
| fd); // Read
11 | value &= 0 b11110011 ; // Clear BANK bits
12 | value |= ( mode << 2); // Set BANK bits with user 's choice
13 | virtualWriteRegister ( AS726x_CONTROL_SETUP , value , fd); ←↪
| // Write

14 }

5.2.6 dataAvailable & clearDataAvailable

Das Bit dataAvailble im register todo wird vom Sensor auf 1 gesetzt wenn nach einer Messung neue daten vorhanden sind, Intterupts mu¨ssen dafu¨r ausgeschaltet sein. dataAvailble wird auf 0 gesetzt wenn daten gelsen werden. Wenn eine One-Shot messung im Bankmode 3 durchgefu¨hrt wird sollte das dataAvailble bit mit der Funktion clearDataAvailable auf 0 gesetzt werden, da nicht sicher gestellt ist das die daten vor der Messung gelsen wurden. Es besteht die m¨oglichkeit das sich das bit f¨alschicherweise noch im falsch positiven zustand befindet. Die Funktion dataAvailable gibt den wert des DataAvailable Bit zuru¨ck.

1 // Checks to see if DRDY flag is set in the control setup register 2 // TODO : was bool test retuned 2
3 uint8_t dataAvailable (int fd) {
4 | uint8_t value = virtualReadRegister ( AS726x_CONTROL_SETUP , ←↪
fd);
5 | return ( value & (1 << 1)); // Bit 1 is DATA_RDY

6 }

7
8 // Clears the DRDY flag
9 // Normally this should clear when data registers are read
10 void clearDataAvailable (int fd) {
11 | uint8_t value = virtualReadRegister ( AS726x_CONTROL_SETUP , ←↪
fd);
12 | value &= | << 1); // Set the DATA_RDY bit
13 | virtualWriteRegister ( AS726x_CONTROL_SETUP , value , fd);

14 }

### 5.3 Rohwerte des AS7261 Auslesen

Die in ?? beschrieben 6 Channel des AS7261 werden mit den folgenden Funktionen ausgelesen:

- getX CIE(fd)
- getY CIE(fd)
- getZ CIE(fd)
- getNIR(fd)
- getDark(fd)
- getClear(fd)

Der File Diskritor einer I2C verbindung mit einem AS7261 wird als u¨bergabe parameter erwatet.
Um den Messert auszulesen wir die Funktion getchannel aufgerufen. Der Ru¨ckgabewer ist der 16-Bit Messwert aus dem jewaligen Register vom Datentyp Integer.

### 5.4 getChannel

Da die Messdaten 16-Bit groß sind, der Sensor aber nur u¨ber 8 Bit register verfu¨gt werden 2 aufeinader folgende register ausgelsen und im Big-Andian Format aneinader geheftet. Die Funktion getChannel erwatet einen File Disciptor einer I2C verbindung zu einem Sensor und die adressen des High Bytes Raw Data Registers.

### 5.5 disableInterrupt

Die Funktion disableInterrupt setzt das INT Bit im register AS726x CONTROL SETUP auf 0 um Interrupts aus zu schalten. Da Der Interrupt auf der Sensor Paltiene nicht verbinden ist muss .. toto muss dass wirklich?

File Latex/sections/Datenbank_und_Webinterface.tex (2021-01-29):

Die Messdaten müssen sicher, einfach zugänglich und möglichst Speichereffizent abgelegt werden.
Dafür eigent sich InfluxDB\footnote{\url{http://influxdata.com}} in Kombination mit einem Grafana\footnote{\url{http://Grafana.com}} Webinterface
\subsection{InfluxDB}\label{datenbankundinterface}
InfluxDB ist eine von InfluxData entwikelte Open Source Time Series Database. 
Time Series Database  sind darauf optimeirt, zusammengehörige Paare von Zeit(en) und Wert(en) zu verwalten und zu komprimieren.
InfluxDB hat eine große Benutzer- und Entwicklerbasis. Es gibt vielseitige Interfaces um Daten zu visualisieren, darunter Grafana.
Eine Time Series Database eignet sich für den Messaufbau, da die Spectralmessdaten mit Zeitbezug erfasst werden.
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

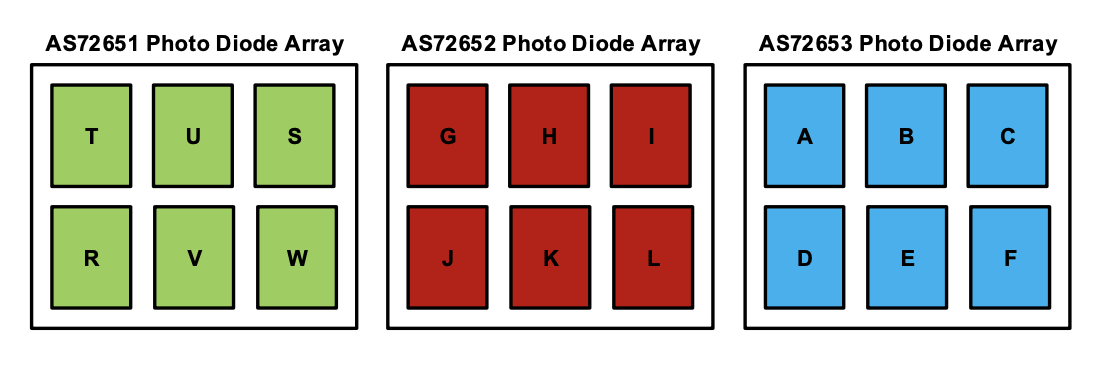
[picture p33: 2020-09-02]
Latex/img/AS7265X-Sensor_Array.png

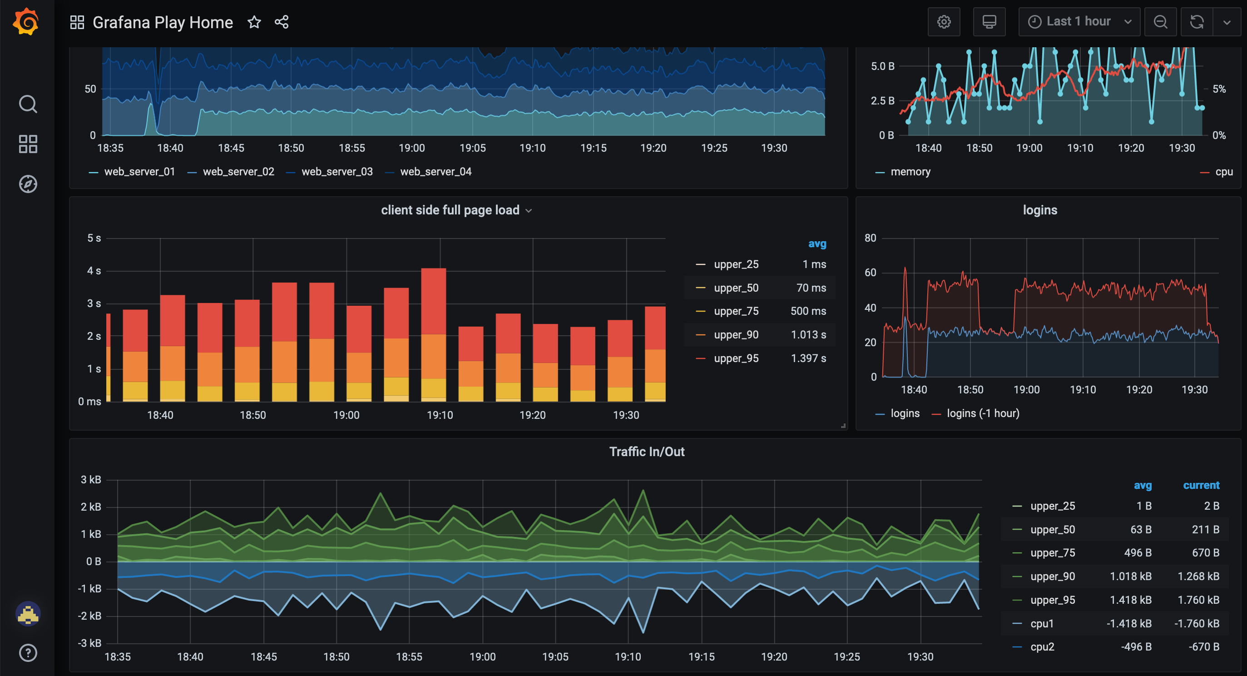
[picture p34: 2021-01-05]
Latex/img/Screenshot 2020-12-23 at 19.34.28.png

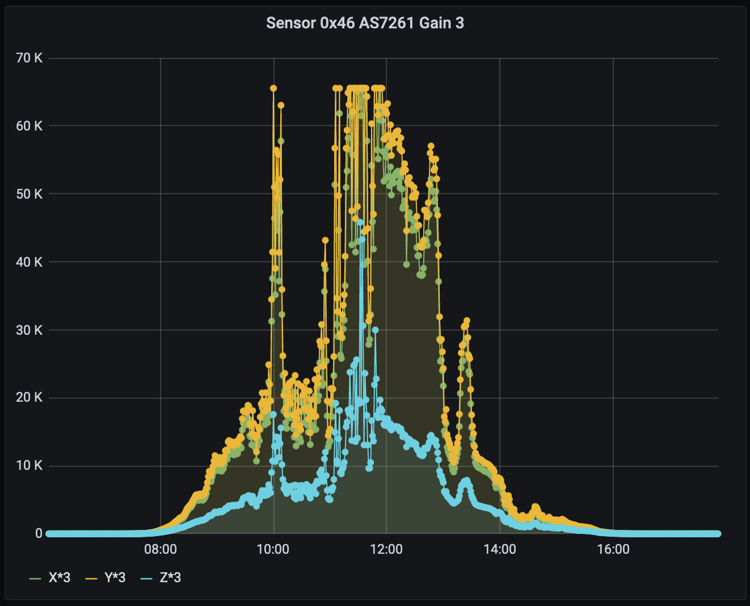
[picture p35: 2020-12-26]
Latex/img/Grafana-Gain3.png

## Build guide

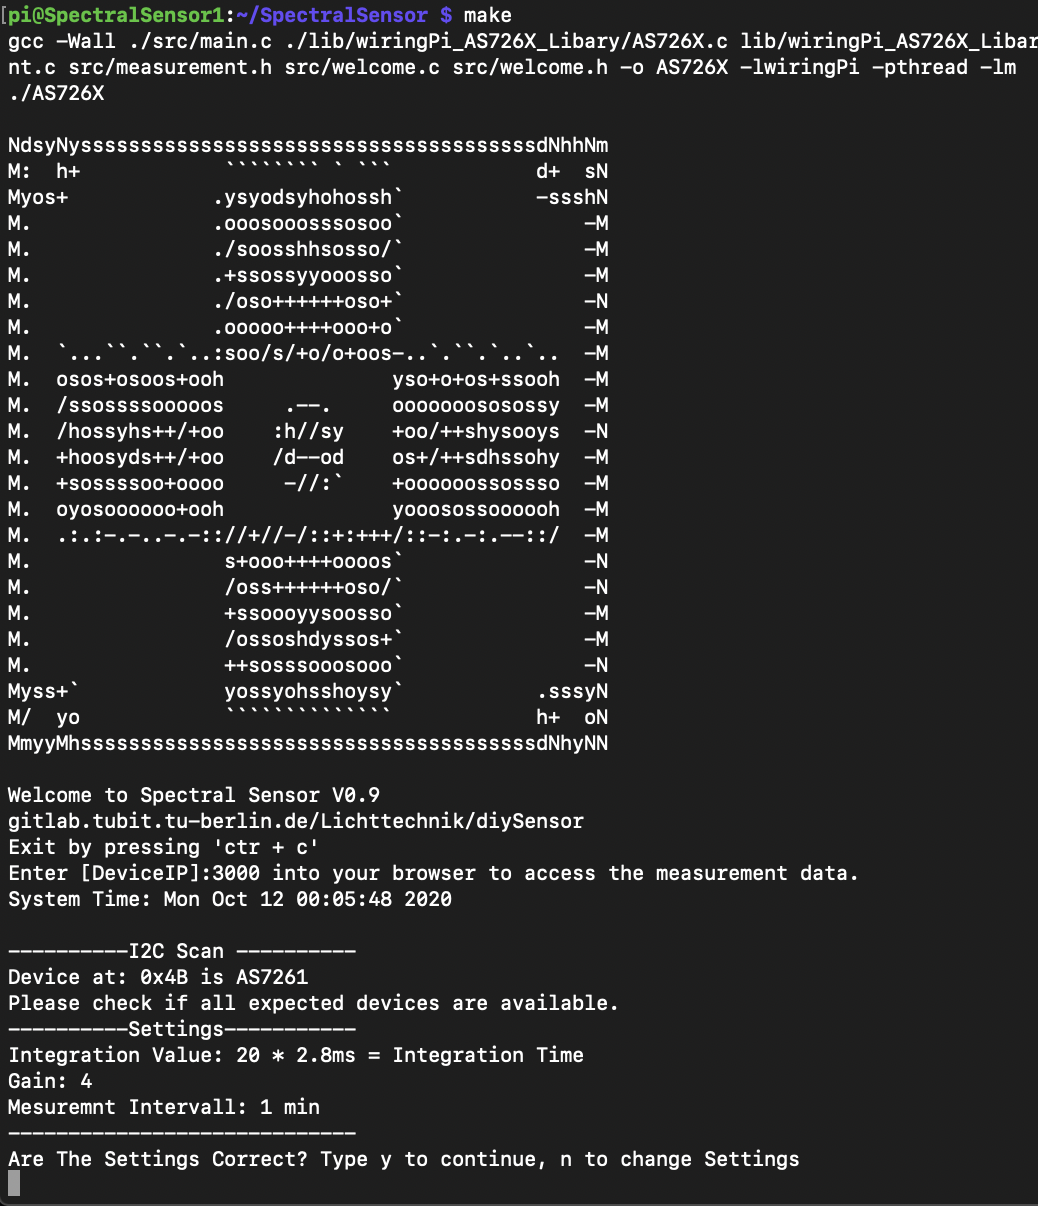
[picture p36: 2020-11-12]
Latex/img/handbuch/make.png

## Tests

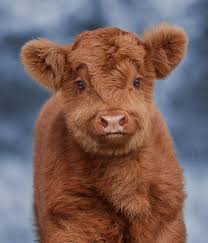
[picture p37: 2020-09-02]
Latex/img/test.jpg

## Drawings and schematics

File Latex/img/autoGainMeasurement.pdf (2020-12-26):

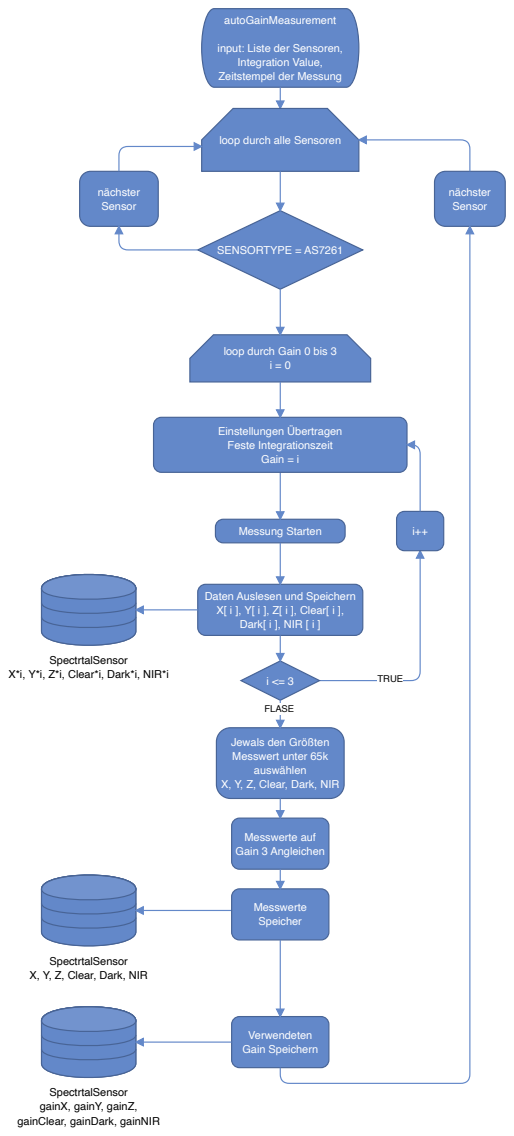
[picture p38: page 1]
autoGainMeasurement; SENSORTYPE = AS7261; Messung Starten; nächster Sensor; Messwerte auf Gain 3 Angleichen; Einstellungen Übertragen Feste Integrationszeit Gain = i; SpectrtalSensor; TRUE; FLASE; Messwerte Speicher; Verwendeten Gain Speichern

input: Liste der Sensoren,
Integration Value,
Zeitstempel der Messung

loop durch alle Sensoren

loop durch Gain 0 bis 3

Daten Auslesen und Speichern
X[ i ], Y[ i ], Z[ i ], Clear[ i ],
Dark[ i ], NIR [ i ]

X*i, Y*i, Z*i, Clear*i, Dark*i, NIR*i

Jewals den Größten
Messwert unter 65k
auswählen
X, Y, Z, Clear, Dark, NIR

SpectrtalSensor

gainX, gainY, gainZ,
gainClear, gainDark, gainNIR

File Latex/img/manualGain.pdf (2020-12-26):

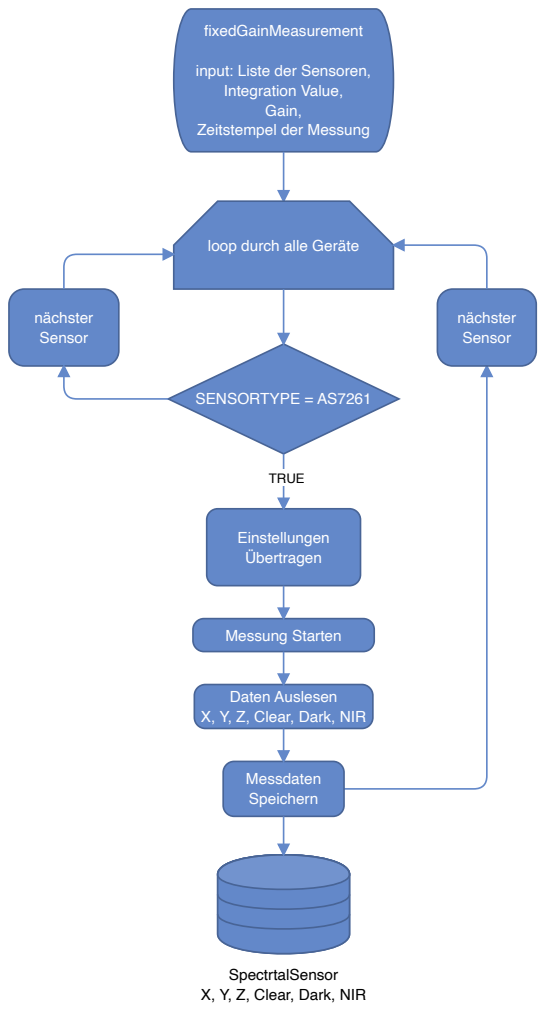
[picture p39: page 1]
fixedGainMeasurement; SENSORTYPE = AS7261; Einstellungen Übertragen; Messung Starten; nächster Sensor; TRUE; Messdaten Speichern

input: Liste der Sensoren,
Integration Value,
Gain,

Zeitstempel der Messung

loop durch alle Geräte

Daten Auslesen
X, Y, Z, Clear, Dark, NIR

SpectrtalSensor

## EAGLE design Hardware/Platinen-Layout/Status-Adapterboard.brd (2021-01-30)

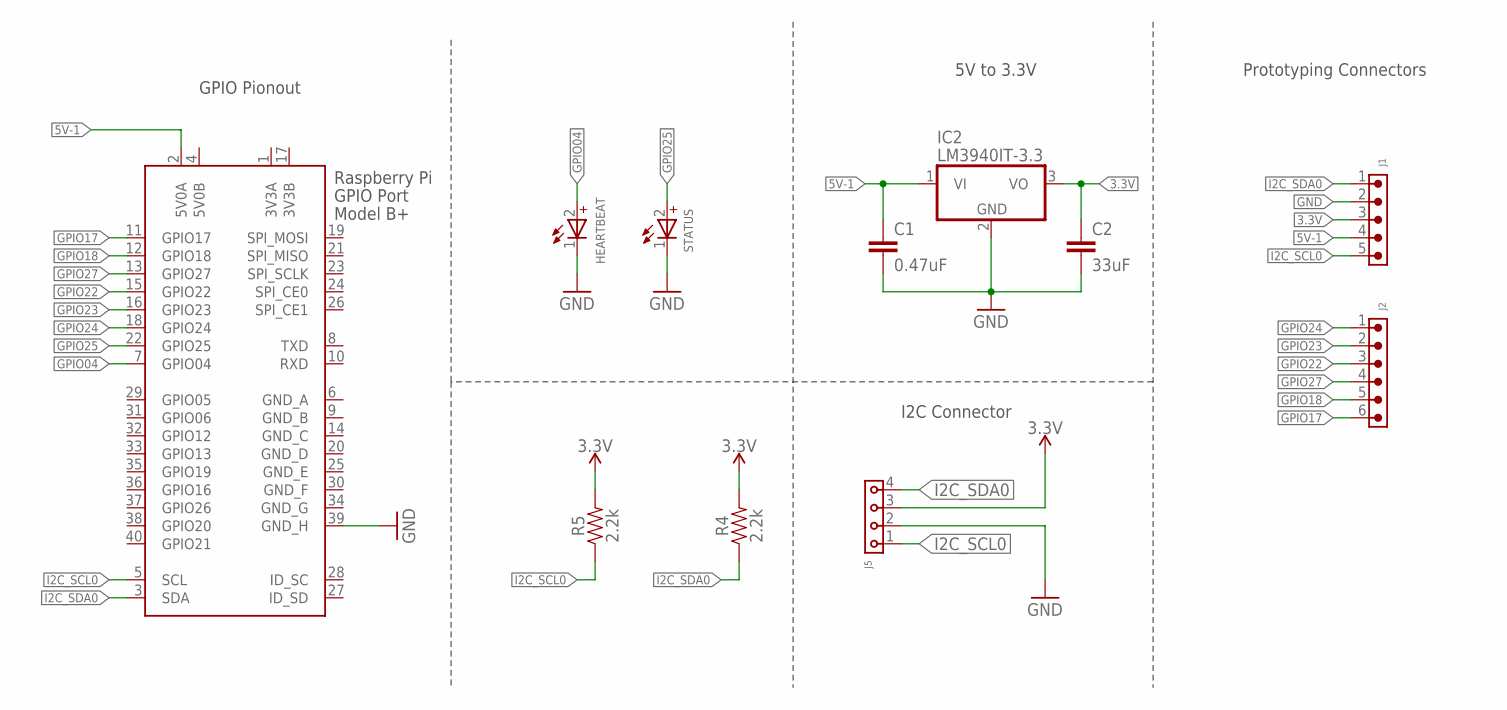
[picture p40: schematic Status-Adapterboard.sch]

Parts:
C1: 0.47uF; 0603
C2: 33uF; C0805
HEARTBEAT: WL-SMSW_0603_REC_155060RS75300; WL-SMSW_0603_REC
IC2: LM3940IT-3.3; TO220H
J1: 6130XX11121_61300511121; 61300511121
J2: 6130XX11121_61300611121; 61300611121
J5: 6130XX11821_61300411821; 61300411821
R4, R5: 2.2k; 0603
STATUS: WL-SMSW_0603_REC_155060GS75300; WL-SMSW_0603_REC
X1: RASPI_BOARD_B+#_HDC; RASPI_BOARD_B+HAT_DF_CF

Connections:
3.3V: C2.1, IC2.3 (VO), J1.3, J5.3, R4.2, R5.2
3V3A: X1.1 (3V3A)
3V3B: X1.17 (3V3B)
5V0B: X1.4 (5V0B)
5V-1: C1.1, IC2.1 (VI), J1.4, X1.2 (5V0A)
GND: C1.2, C2.2, HEARTBEAT.1 (-), IC2.2 (GND), J1.2, J5.2, STATUS.1 (-), X1.39 (GND_H)
GND_A: X1.6 (GND_A)
GND_B: X1.9 (GND_B)
GND_C: X1.14 (GND_C)
GND_D: X1.20 (GND_D)
GND_E: X1.25 (GND_E)
GND_F: X1.30 (GND_F)
GND_G: X1.34 (GND_G)
GPIO04: HEARTBEAT.2 (+), X1.7 (GPIO04)
GPIO17: J2.6, X1.11 (GPIO17)
GPIO18: J2.5, X1.12 (GPIO18)
GPIO22: J2.3, X1.15 (GPIO22)
GPIO23: J2.2, X1.16 (GPIO23)
GPIO24: J2.1, X1.18 (GPIO24)
GPIO25: STATUS.2 (+), X1.22 (GPIO25)
GPIO27: J2.4, X1.13 (GPIO27)
I2C_SCL0: J1.5, J5.1, R5.1, X1.5 (SCL)
I2C_SDA0: J1.1, J5.4, R4.1, X1.3 (SDA)

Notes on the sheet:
I2C Connector
5V to 3.3V
GPIO Pionout
Prototyping Connectors

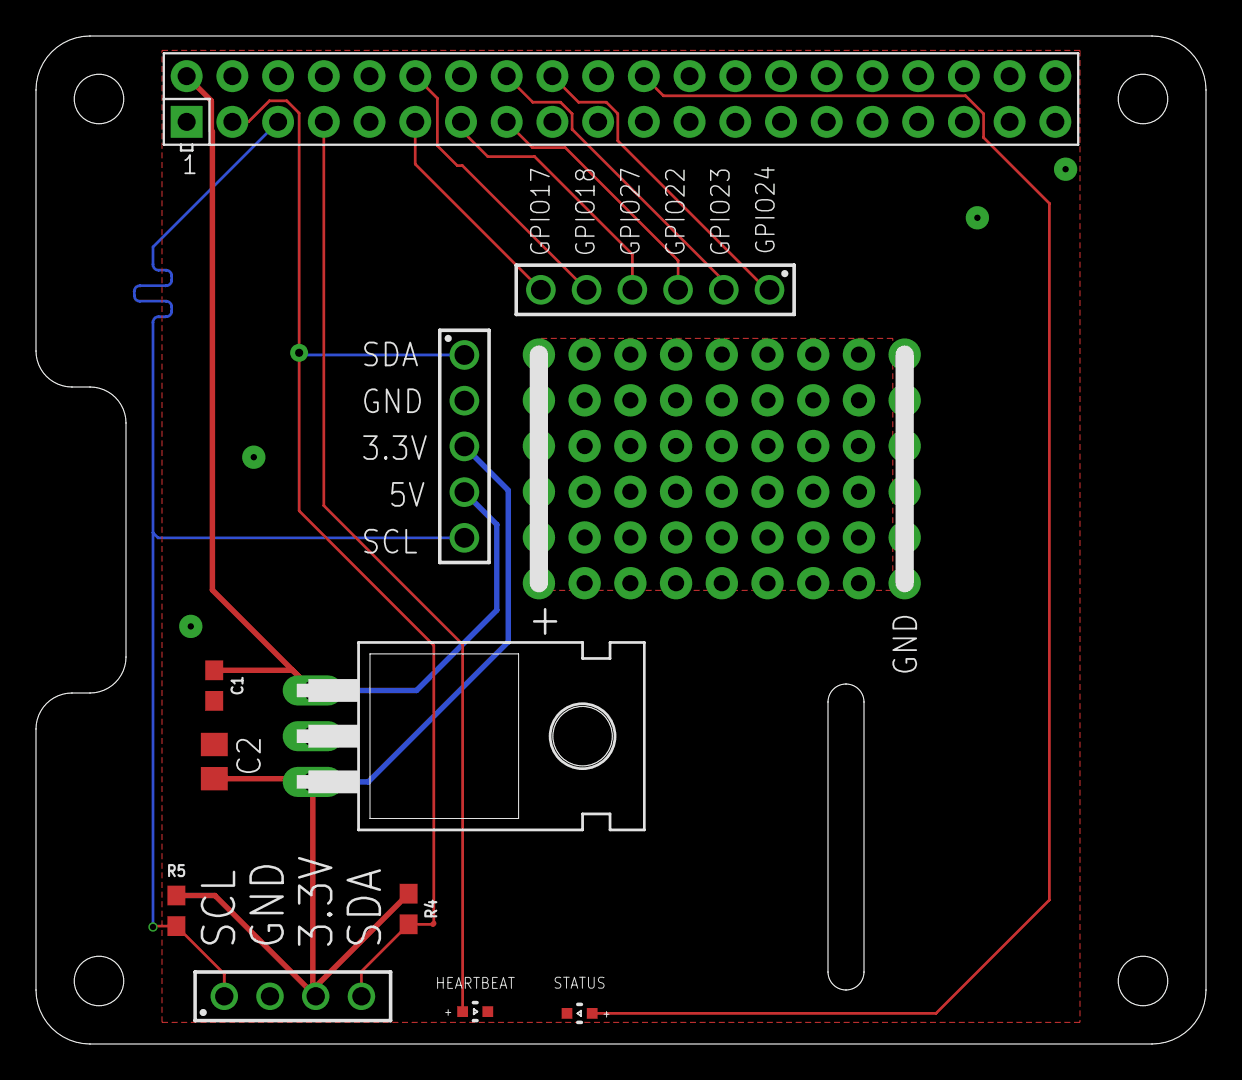
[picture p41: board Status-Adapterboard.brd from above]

Board: 2 copper layers, 65.0 x 56.0 mm, 11 parts (0 on the bottom side), 13 nets.

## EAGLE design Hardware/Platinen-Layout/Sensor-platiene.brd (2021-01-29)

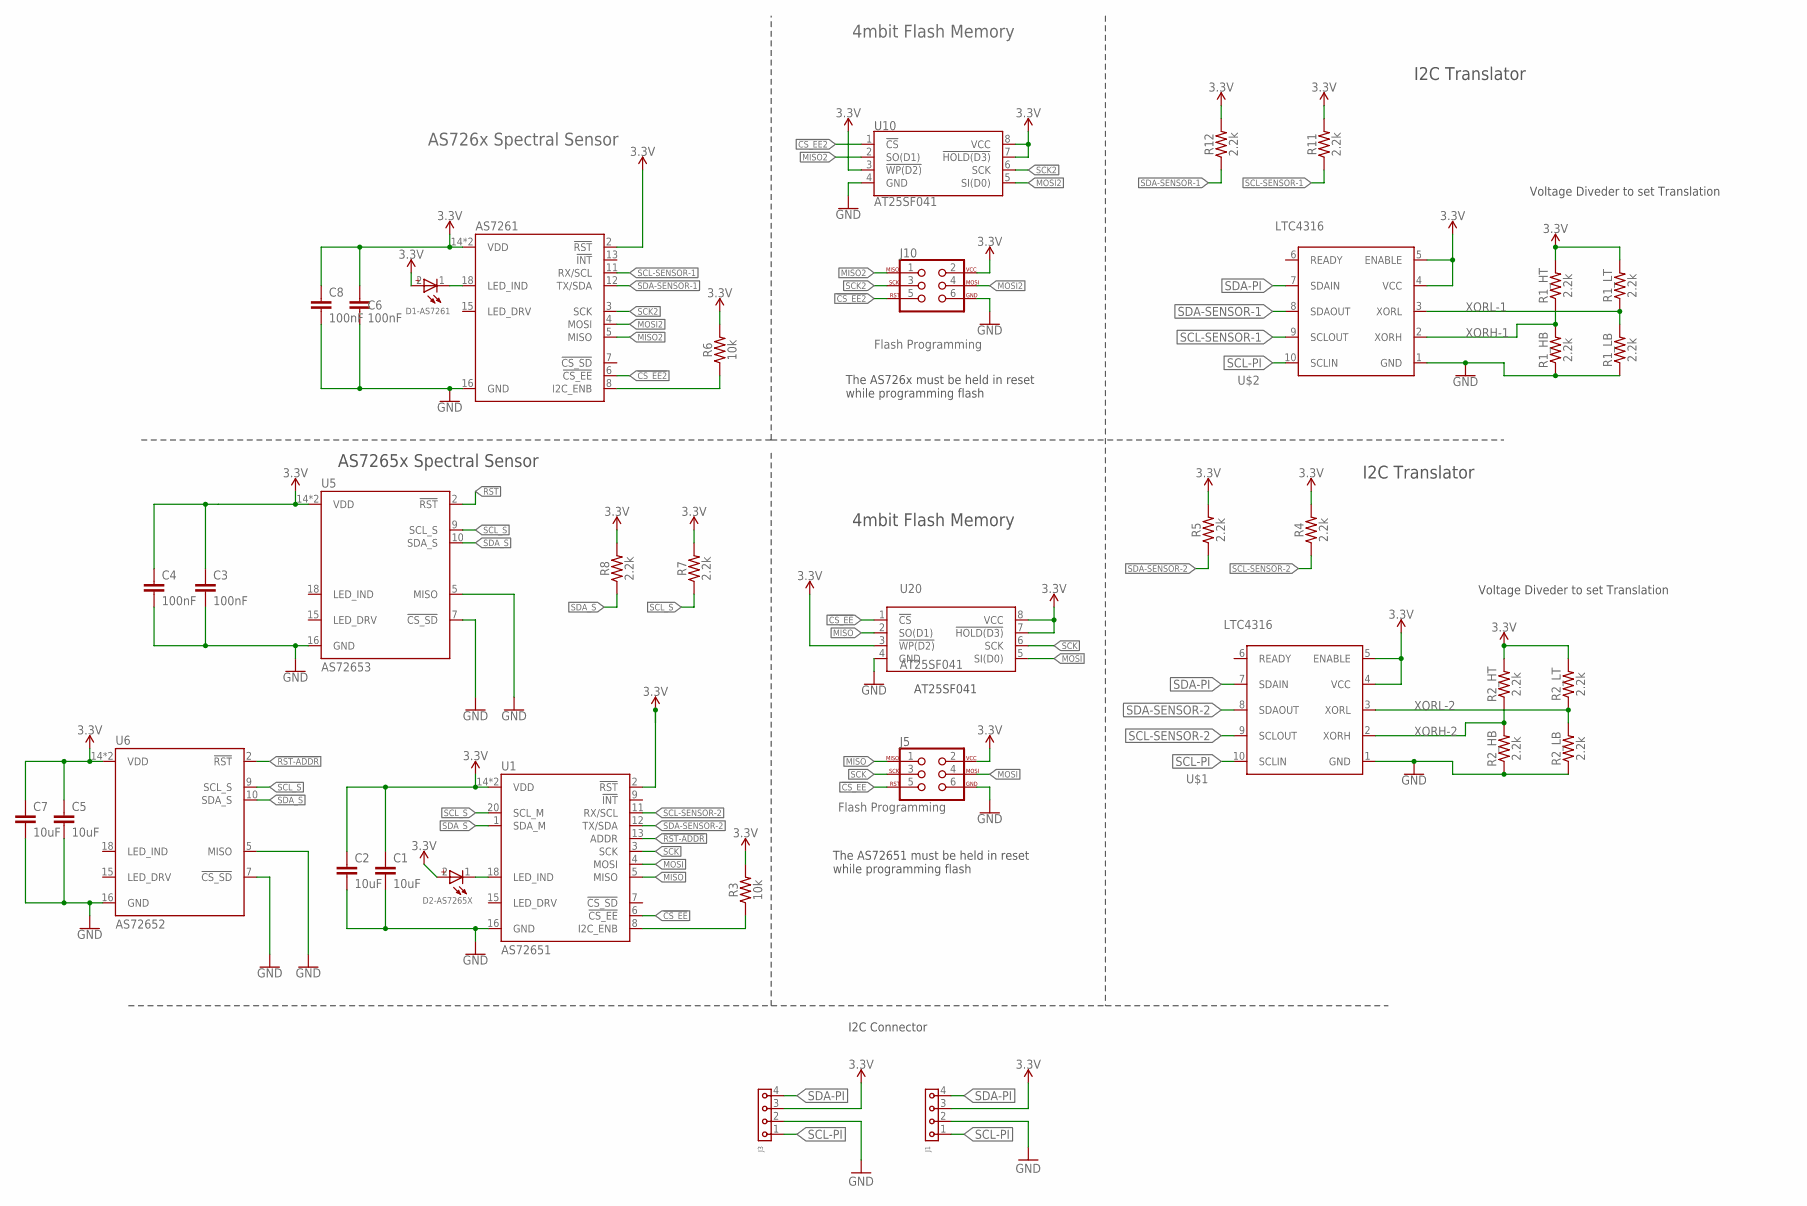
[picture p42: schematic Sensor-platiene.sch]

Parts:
AS7261: IR; LGA20
C1, C2, C5, C7: 10uF; 0603
C3, C4, C6, C8: 100nF; 0603
D1-AS7261, D2-AS7265X: WL-SMCW_1206_150120RS75000; WL-SMCW_1206
J1, J3: 6130XX11821_61300411821; 61300411821
J5, J10: Flash Programming; 2X3_TEST_POINTS
R1_HB, R1_HT, R1_LB, R1_LT, R2_HB, R2_HT, R2_LB, R2_LT, R4, R5, R7, R8, R11, R12: 2.2k; 0603
R3, R6: 10k; 0603
U1: AS72651; LGA20
U5: AS72653; LGA20
U6: AS72652; LGA20
U10, U20: AT25SF041; SO08
U$1, U$2: LTC4316; MS-PACKAGE

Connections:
3.3V: AS7261.2 (!RST), AS7261.14 (VDD), AS7261.17 (VDD), C1.1, C2.1, C3.1, C4.1, C5.1, C6.1, C7.1, C8.1, D1-AS7261.2 (+), D2-AS7265X.2 (+), J1.3, J3.3, J5.2, J10.2, R1_HT.2, R1_LT.2, R2_HT.2, R2_LT.2, R3.2, R4.2, R5.2, R6.2, R7.2, R8.2, R11.2, R12.2, U1.2 (!RST), U1.14 (VDD), U1.17 (VDD), U5.14 (VDD), U5.17 (VDD), U6.14 (VDD), U6.17 (VDD), U10.3 (!WP(D2)), U10.7 (!HOLD(D3)), U10.8 (VCC), U20.3 (!WP(D2)), U20.7 (!HOLD(D3)), U20.8 (VCC), U$1.4 (VCC), U$1.5 (ENABLE), U$2.4 (VCC), U$2.5 (ENABLE)
!CS_EE: J5.5, U1.6 (!CS_EE), U20.1 (!CS)
!CS_EE2: AS7261.6 (!CS_EE), J10.5, U10.1 (!CS)
!RST: U5.2 (!RST)
!RST-ADDR: U1.13 (ADDR), U6.2 (!RST)
GND: AS7261.16 (GND), C1.2, C2.2, C3.2, C4.2, C5.2, C6.2, C7.2, C8.2, J1.2, J3.2, J5.6, J10.6, R1_HB.1, R1_LB.1, R2_HB.1, R2_LB.1, U1.16 (GND), U5.5 (MISO), U5.7 (!CS_SD), U5.16 (GND), U6.5 (MISO), U6.7 (!CS_SD), U6.16 (GND), U10.4 (GND), U20.4 (GND), U$1.1 (GND), U$2.1 (GND)
I2C_ENB: R3.1, U1.8 (I2C_ENB)
MISO: J5.1, U1.5 (MISO), U20.2 (SO(D1))
MISO2: AS7261.5 (MISO), J10.1, U10.2 (SO(D1))
MOSI: J5.4, U1.4 (MOSI), U20.5 (SI(D0))
MOSI2: AS7261.4 (MOSI), J10.4, U10.5 (SI(D0))
unnamed: AS7261.18 (LED_IND), D1-AS7261.1 (-)
unnamed: D2-AS7265X.1 (-), U1.18 (LED_IND)
unnamed: AS7261.8 (I2C_ENB), R6.1
SCK: J5.3, U1.3 (SCK), U20.6 (SCK)
SCK2: AS7261.3 (SCK), J10.3, U10.6 (SCK)
SCL-PI: J1.1, J3.1, U$1.10 (SCLIN), U$2.10 (SCLIN)
SCL-SENSOR-1: AS7261.11 (RX/SCL), R11.1, U$2.9 (SCLOUT)
SCL-SENSOR-2: R4.1, U1.11 (RX/SCL), U$1.9 (SCLOUT)
SCL_S: R7.1, U1.20 (SCL_M), U5.9 (SCL_S), U6.9 (SCL_S)
SDA-PI: J1.4, J3.4, U$1.7 (SDAIN), U$2.7 (SDAIN)
SDA-SENSOR-1: AS7261.12 (TX/SDA), R12.1, U$2.8 (SDAOUT)
SDA-SENSOR-2: R5.1, U1.12 (TX/SDA), U$1.8 (SDAOUT)
SDA_S: R8.1, U1.1 (SDA_M), U5.10 (SDA_S), U6.10 (SDA_S)
XORH-1: R1_HB.2, R1_HT.1, U$2.2 (XORH)
XORH-2: R2_HB.2, R2_HT.1, U$1.2 (XORH)
XORL-1: R1_LB.2, R1_LT.1, U$2.3 (XORL)
XORL-2: R2_LB.2, R2_LT.1, U$1.3 (XORL)

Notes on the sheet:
AS7265x Spectral Sensor
4mbit Flash Memory
The AS72651 must be held in reset while programming flash
AT25SF041
AS726x Spectral Sensor
The AS726x must be held in reset while programming flash
I2C Translator
Voltage Diveder to set Translation
I2C Connector

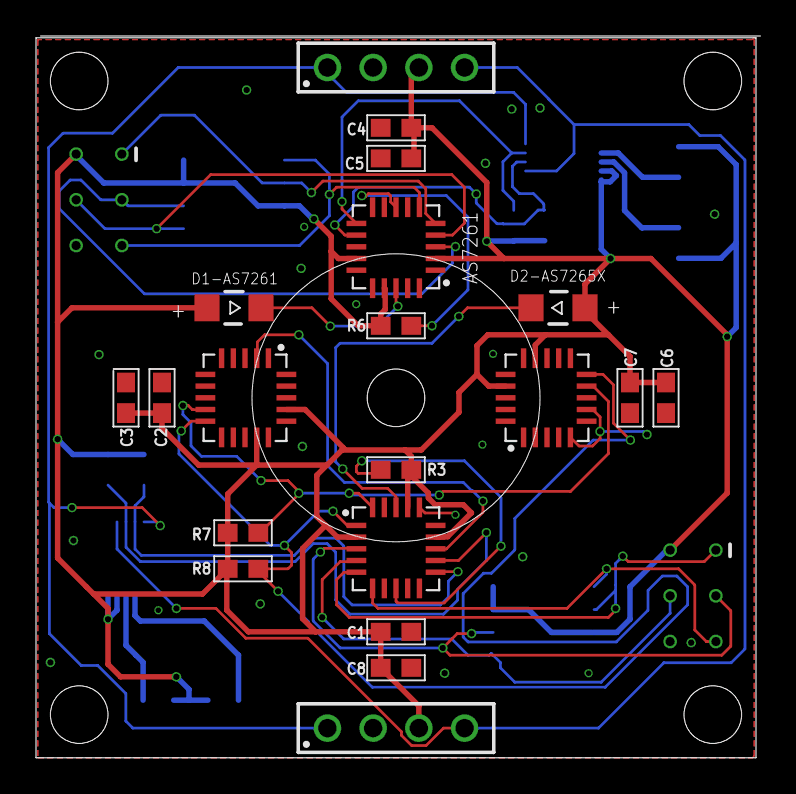
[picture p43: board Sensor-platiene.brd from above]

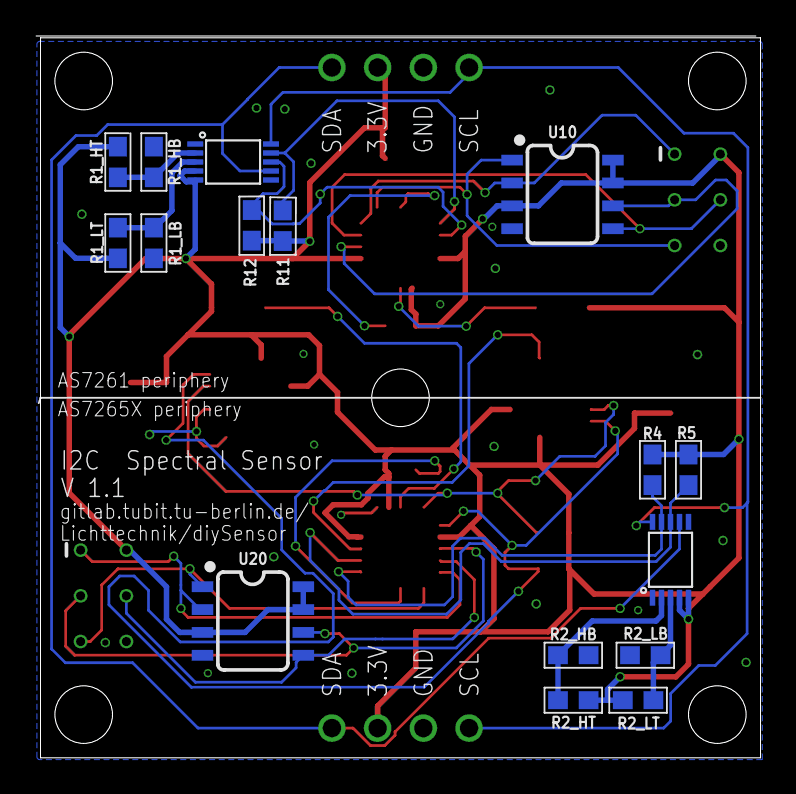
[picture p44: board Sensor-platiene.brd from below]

Board: 2 copper layers, 40.0 x 40.0 mm, 43 parts (18 on the bottom side), 27 nets.

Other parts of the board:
U$3, U$4, U$5, U$6, U$7: 3-2MM-HOLE

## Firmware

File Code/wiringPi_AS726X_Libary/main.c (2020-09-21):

#include <stdio.h>
#include <stdint.h>
#include <wiringPi.h>
#include <wiringPiI2C.h>
#include <sys/time.h> 
#include <stdint.h>
#include "AS726X.h"
#include "influxdb.h"
#include "welcome.h"

struct measurmentSettings{
    uint8_t integrationValue; //Give this function a uint8_t from 0 to 255. //Time will be 2.8ms * [integration value]
    uint8_t gain; //Gain 0: 1x (power-on default) //Gain 1: 3.7x //Gain 2: 16x //Gain 3: 64x
    uint16_t MesuremntIntervall; //in min
};
typedef struct measurmentSettings measurmentSettings;

//returns current epoch time in ms
uint64_t current_timestamp() {
    struct timeval te; 
    gettimeofday(&te, NULL); // get current time
    uint64_t milliseconds = te.tv_sec*1000LL + te.tv_usec/1000; // calculate milliseconds
    return milliseconds;
}

//Delays for given amount of minutes
void delayMesuremntMin(uint16_t MesuremntIntervall){
    time_t current_time;
    time_t next_mesuremnt;
    struct tm * timeinfo;
    time (&next_mesuremnt);                     // save current time to next_mesuremnt
    next_mesuremnt += MesuremntIntervall * 60;  // add MesuremntIntervall to current time 
    timeinfo = localtime ( &next_mesuremnt );   // convert next_mesuremnt time to tm struct 
    printf ( "Next Mesuremnt: %s", asctime (timeinfo) );
    do{                                         // wait until next measurement time is reached
    time (&current_time);                       // save current time to current_time
    } while(next_mesuremnt > current_time);     

}


void saveAS7261Mesurements(int address, uint64_t measurment_time){
    int fd =  wiringPiI2CSetup(address);
    if (fd == -1) {
        printf("i2c failed");
    }
    // Save X
    int X = getX(fd);
    printf ( "0x%X getX: %d",address,X);
    writeToDatabase("X",address,measurment_time,X);
    // Save Y
    int Y = getY(fd);
    printf ( "0x%X getY: %d",address,Y);
    writeToDatabase("Y",address,measurment_time,Y);
    // Save Z
    int Z = getZ(fd);
    printf ( "0x%X getZ: %d",address,Z);
    writeToDatabase("Z",address,measurment_time,Z);

    //Save Clear
    int Clear = getClear(fd);
    printf( "0x%X getClear: %d",address,Clear);
    writeToDatabase("Clear",address,measurment_time,Clear);
    //Save Dark
    int Dark = getDark(fd);
    printf( "0x%X getDark: %d",address,Dark);
    writeToDatabase("Dark",address,measurment_time,Dark);
    //Save NIR
    int NIR = getNIR(fd);
    printf("0x%X getNIR: %d",address,NIR);
    writeToDatabase("NIR",address,measurment_time,NIR);

    //Save Cal_X
    float Cal_X = getCalibratedX(fd);
    printf("0x%X get Cal_X: %f",address , Cal_X);
    writeToDatabase("Cal_X",address,measurment_time, Cal_X);
    //Save Cal_Y
    float Cal_Y = getCalibratedY(fd);
    printf("0x%X get Cal_Y: %f",address , Cal_Y);
    writeToDatabase("Cal_Y",address,measurment_time, Cal_Y);
    //Save Cal_Z
    float Cal_Z = getCalibratedZ(fd);
    printf("0x%X get Cal_Z: %f",address , Cal_Z);
    writeToDatabase("Cal_Z",address,measurment_time, Cal_Z);
    //Save LUX
    uint32_t Cal_LUX = getCalibratedLUX(fd);
    printf("0x%X getLUX: %lu",address , (unsigned long)Cal_LUX);
    writeToDatabase("Cal_LUX",address,measurment_time, Cal_LUX);
    //Save CCT
    uint32_t Cal_CCT = getCalibratedCCT(fd);
    printf("0x%X getCCT: %lu",address , (unsigned long)Cal_CCT);
    writeToDatabase("Cal_CCT",address,measurment_time, Cal_CCT);

    close(fd);
}

void saveAS7265XMesurements(int address, uint64_t measurment_time){
    int fd =  wiringPiI2CSetup(address);
    if (fd == -1) {
        printf("i2c failed");
    }
    // AS7261
    // Save R
    int R = getR(fd);
    printf ( "0x%X getR: %d",address,R);
    writeToDatabase("R",address,measurment_time,R);
    // Save S
    int S = getS(fd);
    printf ( "0x%X getS: %d",address,S);
    writeToDatabase("S",address,measurment_time,S);
    // Save T
    int T = getT(fd);
    printf ( "0x%X getT: %d",address,T);
    writeToDatabase("T",address,measurment_time,T);
    // Save U
    int U = getU(fd);
    printf ( "0x%X getU: %d",address,U);
    writeToDatabase("U",address,measurment_time,U);
    // Save V
    int V = getV(fd);
    printf ( "0x%X getV: %d",address,V);
    writeToDatabase("V",address,measurment_time,V);
    // Save W
    int W = getW(fd);
    printf ( "0x%X getW: %d",address,W);
    writeToDatabase("W",address,measurment_time,W);

    // AS7262
    // Save G
    int G = getG(fd);
    printf ( "0x%X getG: %d",address,G);
    writeToDatabase("G",address,measurment_time,G);
    // Save H
    int H = getH(fd);
    printf ( "0x%X getH: %d",address,H);
    writeToDatabase("H",address,measurment_time,H);
    // Save I
    int I = getI(fd);
    printf ( "0x%X getI: %d",address,I);
    writeToDatabase("I",address,measurment_time,I);
    // Save J
    int J = getJ(fd);
    printf ( "0x%X getJ: %d",address,J);
    writeToDatabase("J",address,measurment_time,J);
    // Save K
    int K = getK(fd);
    printf ( "0x%X getK: %d",address,K);
    writeToDatabase("K",address,measurment_time,K);
    // Save L
    int L = getL(fd);
    printf ( "0x%X getL: %d",address,L);
    writeToDatabase("L",address,measurment_time,L);

    //AS72653
    // Save A
    int A = getA(fd);
    printf ( "0x%X getA: %d",address,A);
    writeToDatabase("A",address,measurment_time,A);
    // Save B
    int B = getB(fd);
    printf ( "0x%X getB: %d",address,B);
    writeToDatabase("B",address,measurment_time,B);
    // Save C
    int C = getC(fd);
    printf ( "0x%X getC: %d",address,C);
    writeToDatabase("C",address,measurment_time,C);
    // Save D
    int D = getD(fd);
    printf ( "0x%X getD: %d",address,D);
    writeToDatabase("D",address,measurment_time,D);
    // Save E
    int E = getE(fd);
    printf ( "0x%X getE: %d",address,E);
    writeToDatabase("E",address,measurment_time,E);
    // Save F
    int F = getF(fd);
    printf ( "0x%X getF: %d",address,F);
    writeToDatabase("F",address,measurment_time,F);

    // Save Cal_R
    float Cal_R = getCalibratedR(fd);
    printf ( "0x%X getCal_R: %f",address,Cal_R);
    writeToDatabase("Cal_R",address,measurment_time,Cal_R);
    // Save Cal_S
    float Cal_S = getCalibratedS(fd);
    printf ( "0x%X getCal_S: %f",address,Cal_S);
    writeToDatabase("Cal_S",address,measurment_time,Cal_S);
    // Save Cal_T
    float Cal_T = getCalibratedT(fd);
    printf ( "0x%X getCal_T: %f",address,Cal_T);
    writeToDatabase("Cal_T",address,measurment_time,Cal_T);
    // Save Cal_U
    float Cal_U = getCalibratedU(fd);
    printf ( "0x%X getCal_U: %f",address,Cal_U);
    writeToDatabase("Cal_U",address,measurment_time,Cal_U);
    // Save Cal_V
    float Cal_V = getCalibratedV(fd);
    printf ( "0x%X getCal_V: %f",address,Cal_V);
    writeToDatabase("Cal_V",address,measurment_time,Cal_V);
    // Save Cal_W
    float Cal_W = getCalibratedW(fd);
    printf ( "0x%X getCal_W: %f",address,Cal_W);
    writeToDatabase("Cal_W",address,measurment_time,Cal_W);
    // Save Cal_G
    float Cal_G = getCalibratedG(fd);
    printf ( "0x%X getCal_G: %f",address,Cal_G);
    writeToDatabase("Cal_G",address,measurment_time,Cal_G);
    // Save Cal_X
    float Cal_H = getCalibratedH(fd);
    printf ( "0x%X getCal_H: %f",address,Cal_H);
    writeToDatabase("Cal_H",address,measurment_time,Cal_H);
    // Save Cal_I
    float Cal_I = getCalibratedI(fd);
    printf ( "0x%X getCal_I: %f",address,Cal_I);
    writeToDatabase("Cal_I",address,measurment_time,Cal_I);
    // Save Cal_J
    float Cal_J = getCalibratedJ(fd);
    printf ( "0x%X getCal_J: %f",address,Cal_J);
    writeToDatabase("Cal_J",address,measurment_time,Cal_J);
    // Save Cal_K
    float Cal_K = getCalibratedK(fd);
    printf ( "0x%X getCal_K: %f",address,Cal_K);
    writeToDatabase("Cal_K",address,measurment_time,Cal_K);
    // Save Cal_L
    float Cal_L = getCalibratedL(fd);
    printf ( "0x%X getCal_L: %f",address,Cal_L);
    writeToDatabase("Cal_L",address,measurment_time,Cal_L);
    // Save Cal_A
    float Cal_A = getCalibratedA(fd);
    printf ( "0x%X getCal_A: %f",address,Cal_A);
    writeToDatabase("Cal_A",address,measurment_time,Cal_A);
    // Save Cal_B
    float Cal_B = getCalibratedB(fd);
    printf ( "0x%X getCal_B: %f",address,Cal_B);
    writeToDatabase("Cal_B",address,measurment_time,Cal_B);
    // Save Cal_C
    float Cal_C = getCalibratedC(fd);
    printf ( "0x%X getCal_C: %f",address,Cal_C);
    writeToDatabase("Cal_C",address,measurment_time,Cal_C);
    // Save Cal_D
    float Cal_D = getCalibratedD(fd);
    printf ( "0x%X getCal_D: %f",address,Cal_D);
    writeToDatabase("Cal_D",address,measurment_time,Cal_D);
    // Save Cal_E
    float Cal_E = getCalibratedE(fd);
    printf ( "0x%X getCal_E: %f",address,Cal_E);
    writeToDatabase("Cal_E",address,measurment_time,Cal_E);
    // Save Cal_F
    float Cal_F = getCalibratedF(fd);
    printf ( "0x%X getCal_F: %f",address,Cal_F);
    writeToDatabase("Cal_F",address,measurment_time,Cal_F);



    close(fd);
}
uint64_t MeasurementFromAllAdresses(sensor_list *const s){
    int i=0;
    uint64_t measurment_time = current_timestamp(); // save measurment time
    while(s[i].address != -1 && i < 128){ // take Measurements from all available Sensors
            MeasurementFromAdress(s[i].address);
            i++;
    }
    uint64_t measurment_duration = current_timestamp()-measurment_time; // save measurment time
    printf("Measurment Duration: %lu ms\n", measurment_duration);
    return measurment_time;
}

void settings(int address, uint8_t integrationValue, uint8_t gain){
    int fd =  wiringPiI2CSetup(address);
    if (fd == -1) {
        printf("i2c failed");
    }
    disableInterrupt(fd);
    setIntegrationTime(integrationValue, fd);
    setGain(gain, fd); 
    close(fd);
}

void changeSettings(measurmentSettings *Settings){
    printf("\n\n\n\n\n");
    char tmp[10];    //define teporary input storage

    do{
    printf("Set Integration Value [0:255]:\n");
    fgets(tmp,10,stdin);
    } while(!(atoi(tmp)>=0 && atoi(tmp)<=255));
    Settings->integrationValue = atoi(tmp);

    do{
    printf("Set Gain [0:3] 0->1x 1->3.7x 2->16x 3->64x:\n");
    fgets(tmp,10,stdin);
    } while(!(atoi(tmp)>=0 && atoi(tmp)<=3));
    Settings->gain = atoi(tmp);

    do{
    printf("Set Mesuremnt Intervall in Minutes [1:65535]\n");
    fgets(tmp,10,stdin);
    } while(!(atoi(tmp)>=1 && atoi(tmp)<=65535));
    Settings->MesuremntIntervall = atoi(tmp); 

    printf("\n\n\n\n\n");

}
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

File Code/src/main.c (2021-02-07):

#include <stdio.h>
#include <stdint.h>
#include <stdlib.h>
#include <string.h>
#include <wiringPi.h>
#include <wiringPiI2C.h>
#include <sys/time.h> 
#include <math.h>
#include "../lib/wiringPi_AS726X_Libary/AS726X.h"
#include "../lib/influxDB_http_Libary/influxdb.h"
#include "measurement.h"
#include "welcome.h"
#include "../default_values.h"

#define AUTOGAIN 4
#define HEARTBEAT_LED 7
#define STATUS_LED 6

struct measurmentSettings{
    uint8_t integrationValue;       // Value from 0-255 -> Integration Time will be 2.8ms * [integration value] 
    uint8_t gain;                   // Gain 0: 1x (power-on default) //Gain 1: 3.7x //Gain 2: 16x //Gain 3: 64x
    uint16_t measurementIntervall;  // Interval of the measurement, the measurement always takes place at the second 0
};
typedef struct measurmentSettings measurmentSettings;

// returns the current epoch time in ms
uint64_t currentTimestamp() {
    struct timeval te;        // struct with microsecond precision
    gettimeofday(&te, NULL);  // get current time
    uint64_t milliseconds = te.tv_sec*1000LL + te.tv_usec/1000; // calculate milliseconds
    return milliseconds;
}

// Delays for given amount of minutes
void delayMeasurementMin(uint16_t measurementIntervall){
    if (measurementIntervall >= 1){
        time_t current_time;                        			// Curren time for comparison
        time_t next_measurement;                      			// Calculated time for the next measurement
        struct tm * next_measurement_tm;              			// tm struct for next measurement calculation
        time (&next_measurement);                     			// Save current time to next_measurement
        next_measurement_tm = localtime ( &next_measurement );  // Convert next_measurement time to tm struct 
        next_measurement_tm->tm_min += measurementIntervall;    // Add Intervall to next_measurement tm struct
        next_measurement_tm->tm_sec = 0;                      	// Set sec of next_measurement tm struct to zero
        mktime(next_measurement_tm);                          	// Normalize struct (for example min: 61->1)
        next_measurement = mktime(next_measurement_tm);         // Convert next_measurement_tm  back to time_t

        printf ("Next measurement: %s", asctime (next_measurement_tm));
        do{                                         // Wait until next measurement time is reached
        time (&current_time);                       // Save current time to current_time
        } while(next_measurement > current_time);
    }
    else{
        printf("invalid waiting Time\n");
    }
}


// Print the current Time
void printTime(){
    time_t current_time;								// time_t struct for current time
    struct tm * timeinfo;  								// tm struct
    time (&current_time); 								// Save current time to current_time
    timeinfo = localtime ( &current_time);				// Convert time_t current_time to tm timeinfo 
    printf ( "System Time: %s\n", asctime (timeinfo));	// Print timeinfo
}

// Writing settings to the data structure at system startup
// This dose not write the settings to the Sensor! it just "collects" the settings to the data structure
// Input pointer to measurmentSettings data structure  
void changeSettings(measurmentSettings *Settings){
    printf("\n\n\n\n\n");
    char tmp[10];    // Define teporary user input storage

    do{
    printf("Set Integration Value [0:255]:\n");
    fgets(tmp,10,stdin);
    } while(!(atoi(tmp)>=0 && atoi(tmp)<=255));
    Settings->integrationValue = atoi(tmp);

    do{
    printf("Set Gain [0:3] 0->1x 1->3.7x 2->16x 3->64x 4->Auto Gain:\n");
    fgets(tmp,10,stdin);
    } while(!(atoi(tmp)>=0 && atoi(tmp)<=4));
    Settings->gain = atoi(tmp);

    do{
    printf("Set measurement Intervall in Minutes [1:65535]:\n");
    printf("(Note that by connecting more than 3 sensors a measurement can sometimes take longer than one minute)\n");
    fgets(tmp,10,stdin);
    } while(!(atoi(tmp)>=1 && atoi(tmp)<=65535));
    Settings->measurementIntervall = atoi(tmp); 

    printf("\n\n\n\n\n");
}
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

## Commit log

2020-05-06 Add notizen
    [Sensorboard.brd, Sensorboard.sch, test-sensior-platiene.sch]
2020-05-27 new lib folder starting to port led working =)
2020-05-30 scematic is done
    [Sensorboard.brd, Sensorboard.sch, test-sensior-platiene.brd, test-sensior-platiene.sch]
2020-05-30 basic hols in board
2020-05-30 board alingnment done
2020-05-30 board is a mess
    [test-sensior-platiene.brd, test-sensior-platiene.sch]
2020-05-31 board is getting there
    [test-sensior-platiene.brd, test-sensior-platiene.sch]
2020-05-31 board is better
    [test-sensior-platiene.brd, test-sensior-platiene.sch]
2020-05-31 board is better2
    [test-sensior-platiene.brd, test-sensior-platiene.sch]
2020-05-31 almost done
    [test-sensior-platiene.brd]
2020-05-31 almost done2
    [test-sensior-platiene.brd]
2020-05-31 todo ground plane
    [test-sensior-platiene.brd]
2020-05-31 todo ground plane next try
    [test-sensior-platiene.brd]
2020-05-31 board is done TODO: change hole size- shild scematic done
    [Sensor-platiene.brd, Sensorboard.brd, Sensorboard.sch, nanopi-black2-shield.sch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]
2020-06-22 latex template!!!
    [Sensor-platiene.brd, Sensor-platiene.sch, nanopi-black2-shield.brd, nanopi-black2-shield.sch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]
2020-08-11 remove trash
    [Sensor-platiene.brd, Sensor-platiene.sch]
2020-08-21 add write to db
    [Sensor-platiene.brd, Sensor-platiene.sch, nanopi-black2-shield.brd, nanopi-black2-shield.sch]
2020-09-07 add heatsink to board
    [Sensor-platiene.brd]
2020-09-13 new hardware + test code
    [Sensor-platiene.brd, Sensor-platiene.sch, copper_bottom.gbr, copper_top.gbr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]
2020-09-14 sensor detection + read all values + hardware check
2020-09-26 new adapter Board
    [calibrationX.csv, calibrationY.csv, calibrationZ.csv, copper_bottom.gbr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]
2020-09-26 relase 1.1 is comming
    [calibrationA.csv, calibrationB.csv, calibrationC.csv, calibrationD.csv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]
2020-09-26 Version 1.1 Relase - just added shitty features 1.0 is king
    [calibrationA.csv, calibrationB.csv, calibrationC.csv, calibrationD.csv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]
2020-10-11 1.1 release fixed time issue and has a new file structure
    [nanopi-black2-shield.sch]
2020-12-26 latex tex tex
    [nanopi-black2-shield.brd]
2021-01-29 latex todo list
    [Sensor-platiene.brd]
2021-02-07 12 boards working - mux Done
    [Sensorboard.brd, Sensorboard.sch, Status-Adapterboard.brd, Status-Adapterboard.sch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]
2021-03-12 cean up abgabe files
    [Sensorboard.brd, Sensorboard.sch, Status-Adapterboard.brd, Status-Adapterboard.sch]
2021-03-26 add stuff from gitW
    #
    [Sensor-platiene.brd, Sensor-platiene.sch, Status-Adapterboard.brd, Status-Adapterboard.sch]
2021-03-26 Revert "add stuff from gitW"
    This reverts commit b289d961393d5d6742d5daff51f6af8780659001.
    [Sensor-platiene.brd, Sensor-platiene.sch, Status-Adapterboard.brd, Status-Adapterboard.sch]

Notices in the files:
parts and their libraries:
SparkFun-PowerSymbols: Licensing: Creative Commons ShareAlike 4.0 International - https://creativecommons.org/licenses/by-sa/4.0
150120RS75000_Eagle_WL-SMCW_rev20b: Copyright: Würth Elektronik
